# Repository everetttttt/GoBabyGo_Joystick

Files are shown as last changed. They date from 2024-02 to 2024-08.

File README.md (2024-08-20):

# GoBabyGo Joystick Project
### Wichita State University 2024
### Everett Kernen and Jackson Truitt
-----------
-----------

In this tutorial you will learn how to implement a joystick into your GoBabyGo vehicle for supporting children with motor or other disabilities.

## TODO
* add motor controller programmer details
* add linear actuator installation
* add images

You will need
-----------
### If you are at Wichita State, many of these components will already exist in the GoBabyGo room. Check before you purchase.
* [Vehicle](https://www.amazon.com/gp/product/B0C7JK9HNR/ref=ask_ql_qh_dp_hza?th=1)
     - This "Jeep" is the one we used and configured the steering mechanism for. Other ride-on vehicles we have seen use extremely similar electronics, so the only difference should be the steering.
* [Kill switch](https://www.amazon.com/Toggle-Switches-Rocker-Switch-Waterproof/dp/B07WW3WW3F)
* [Arduino Nano Every with headers](https://store-usa.arduino.cc/collections/boards-modules/products/arduino-nano-every-with-headers)
* [Motor Controller](https://www.amazon.com/HOBBYWING-QUICRUN-Waterproof-Brushed-Motors/dp/B07NYBF6MQ)
* [Motor Controller Programmer](https://www.hobbywingdirect.com/products/led-pc2c?variant=172030922)
     - The motor controller settings will be changed lower in this tutorial.
* [Linear Actuator](https://www.servocity.com/4-stroke-25-lb-thrust-linear-servo/)
     - At $300, this is by far the biggest opportunity we have to reduce costs. We are in the process of configuring [this servo,](https://www.amazon.com/GoolRC-Digital-Torque-Waterproof-Replacements/dp/B0B5H4MWZG) but that process is unfinished at this time.
* [Joystick](https://www.amazon.com/Acxico-Joystick-Potentiometer-JH-D202X-R2-Thermistor/dp/B09JZ8ZV4L)
* [RC Controller](https://www.amazon.com/DUMBORC-Transmitter-Receiver-Controller-400m-500m/dp/B07RR81GSB)
     - Used for parent override
* [30A bus bar](https://www.amazon.com/OONO-Position-Terminal-Distribution-Module/dp/B09D3BV22M)
* [4 foot servo wires](https://www.readymaderc.com/products/details/120cm-48in-jr-twisted-22awg-servo-cable?srsltid=AfmBOooBtGZkchE-u-FVPZSh1Mha9t9dLRYeGN2BnarDRjaqf-3A2QVKya4)
     - Quantity 2
* [Potentiometer - speed control](https://www.amazon.com/Uxcell-a15040700ux0380-Terminals-Linear-Potentiometer/dp/B019I13X5K)
* [Potentiometer - steering control](https://www.digikey.com/en/products/detail/bourns-inc/3296W-1-103LF/1088045)
     - Quantity 2
* [15 pin female header pins](https://www.amazon.com/2-54mm-Female-Single-Straight-Header/dp/B07VP63Z78)
     - Connect the arduino to the PCB
* [Male header pins](https://www.amazon.com/HiLetgo-20pcs-2-54mm-Single-Header/dp/B07R5QDL8D)
     - Connect everything else to the PCB
* [Spade connectors](https://www.amazon.com/Connectors-Shrink-Terminals-Female-MENTBERY/dp/B0BFDJNK91?source=ps-sl-shoppingads-lpcontext&ref_=fplfs&smid=A2TBO4E1CS6T20&th=1)
* PCB
     - You can upload the attached [gerber file](/GBG_Joystick_PCB_v4.zip) to a PCB manufacturer of your choice (PCBWay, JLCPCB, among others). You can also see and modify the [KiCAD files](/KiCAD/) and export from there.
     - Alternatively, you could build this on a breadboard or solder all wires together. If you do that, I highly recommend you reference the [schematic](/KiCAD/KiCAD.kicad_sch).
* Access to a soldering iron

## Starting here

After assembling your vehicle, the "engine bay" will look like this.
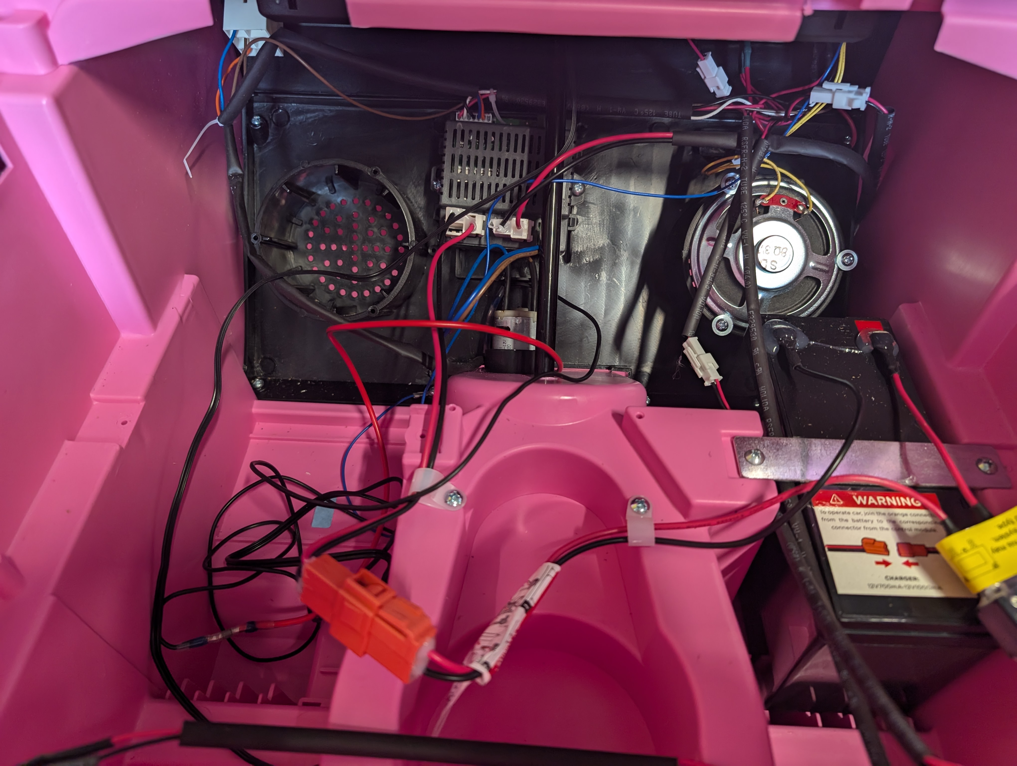
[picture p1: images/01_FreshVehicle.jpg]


It looks like (and is) a jumbled mess of wires, but it's pretty easy to sort out.
Here are the components that are relevant to us.
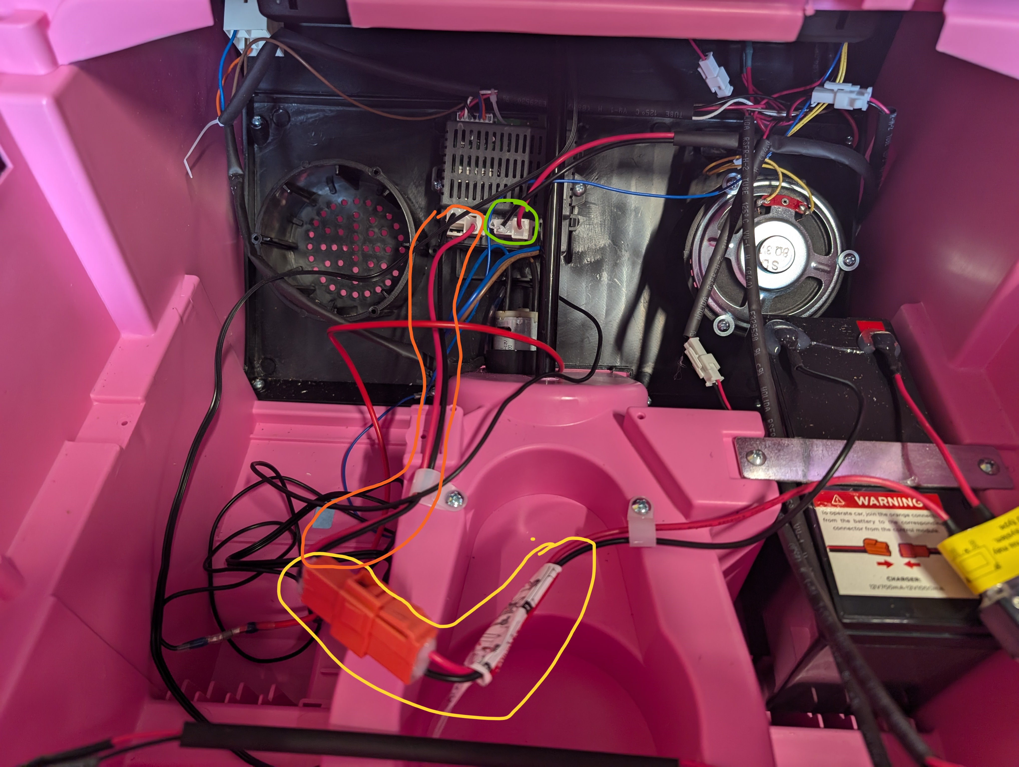
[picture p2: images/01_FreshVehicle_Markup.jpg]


## Step 1: Disassembly
1. Before you do anything, disconnect the battery, wires outlined in yellow.
2. Double check you've disconnected the battery. 
3. Disconnect the connector outlined in green. It heads to the rear motors which power the car.
4. Disconnect the connector leading to the steering motor. The connector is between the green and orange connectors and the wires are typically blue and brown.

## Step 2: Preparation and wiring power
Cut a small board to place all your components on. We used MDF, but it could be rigid cardboard.\
Gather your 30A bus, a spool of wire (14-18AWG), your kill switch, and your 30A bus.

### Preparation
1. Making sure once again that the orange wire is not connected on either side, cut it about three inches from the orange connector. 
2. Strip all four wires about a quarter of an inch
3. Take the red wire on the orange connector side and crimp on a spade connector that fits the wire guage. Once crimped, pull to make sure it is secure.
### Kill switch
4. Taking your spool of wire, strip the same amount from two wires and crimp the opposite spade connector on one. Again, pull to test it's secure, then connect it to the red wire we just crimped.
5. Run both spool wires from your spool to the rear of the car, running the wire along the bottom or side of the car to keep things neat and tidy. 
6. Use wire nuts or spade connectors to connect the wires to your kill switch.
7. Use a drill and the accompanying nuts that came with the switch to attach it securely to the rear of the car.
### 30A bus and motor controller
8. Coming back to the front, take the 30A bus and screw 1) the other wire from the kill switch and 2) the black wire on the orange connector side to the end of the bus. Note which letter is displayed. We used A for positive (red, going from battery positive to kill switch and back) and B for ground (black, battery negative).
9. Ensure the battery remains disconnected, if you connected it to test kill switch continuity.
10. Screw the power wires from the car controller (the other half of the orange wire) into the bus, ensuring A goes with A and B goes with B.
11. With your motor controller, cut and strip the red and black power wires and screw them into the bus.
12. Cut the connector (previously outlined in green) off the wires going to the rear motors. Strip both wires and crimp on spade connectors.
13. On the motor controller, cut and strip one yellow and one blue wire and crimp on the opposing spade connector.
14. Connect the motor controller and rear motor wires.

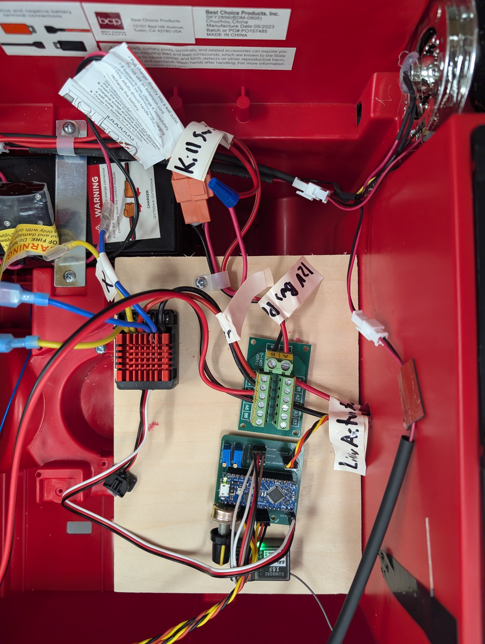
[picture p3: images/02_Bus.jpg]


Now referencing our [KiCAD schematic](images/02_schematic.png), we've completed the following (outlined in blue).
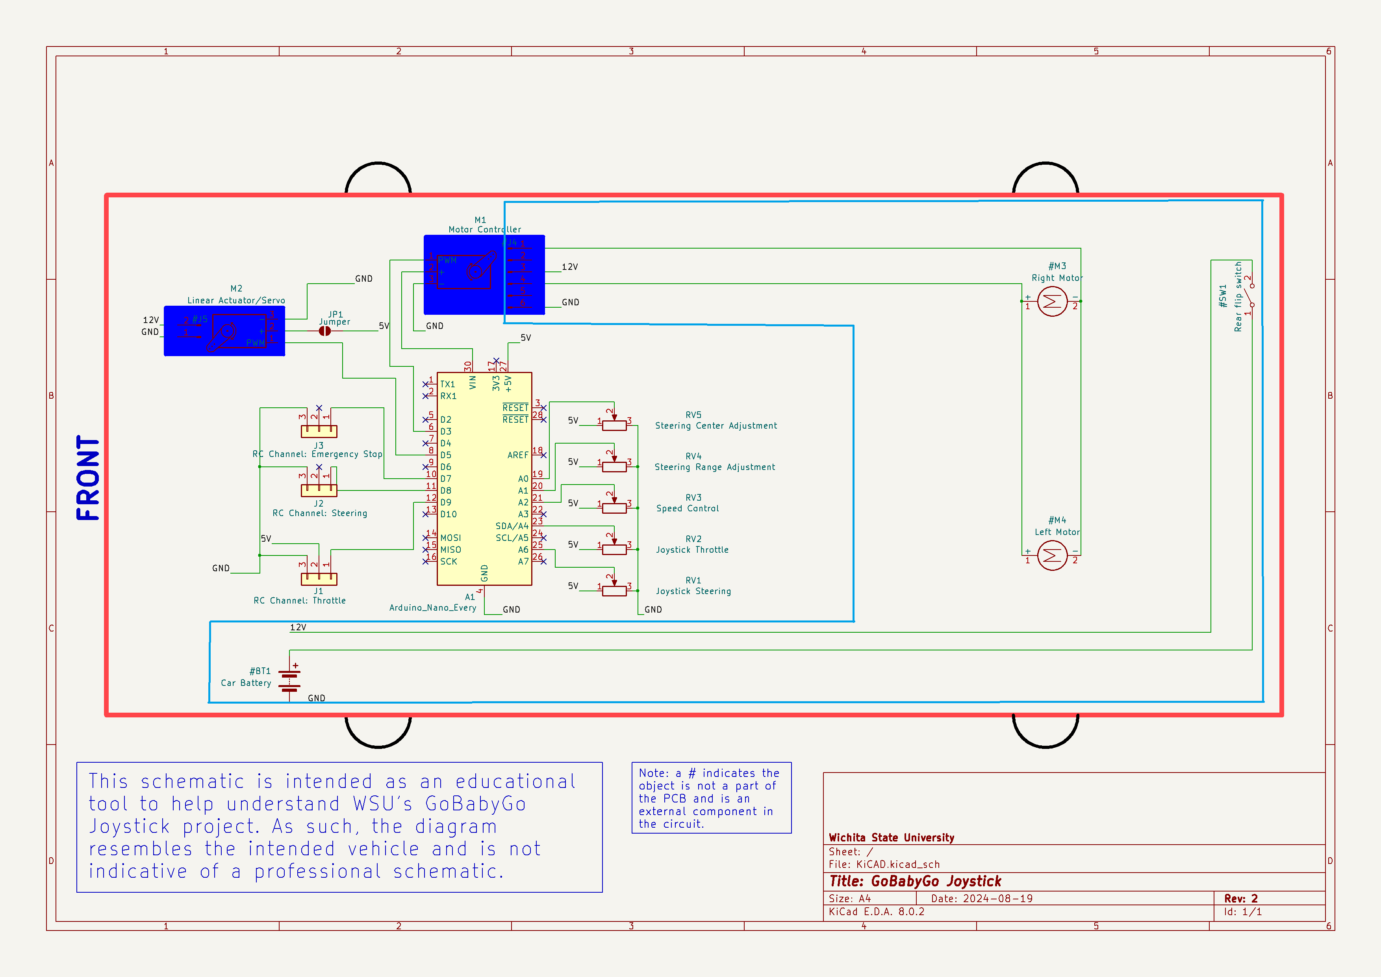
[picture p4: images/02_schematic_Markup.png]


## Step 3: Linear Actuator
### TODO

## Step 4: Joystick soldering
This soldering is easily the most difficult, so be prepared. We recommend grabbing some small heat shrink tubing to go over the wires to insulate and protect the connections.
1. Grab the joystick and two servo wires. Cut the wires and keep the female ends. We keep the female ends here because the 4 foot servo wires will connect their female ends to the male ends on the PCB.
2. Splice the wires, solder them to the joystick leads, and cover with heat shrink tubing.
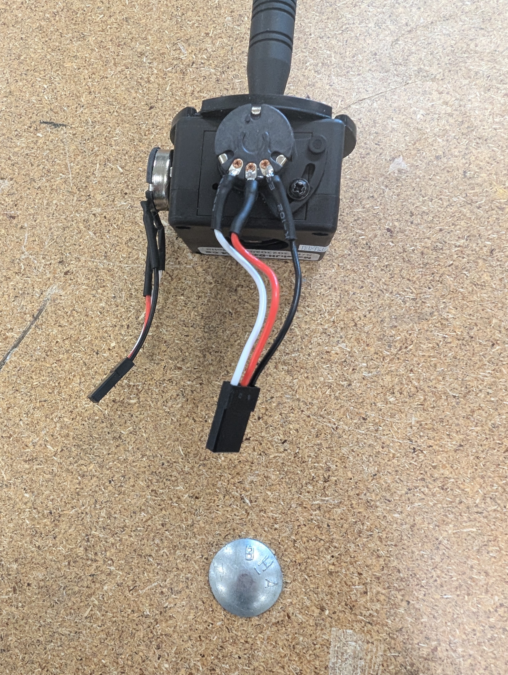
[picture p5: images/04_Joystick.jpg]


## Step 5: PCB
1. Gather your PCB, two 15 pin female headers, seven 3 pin male headers, and all three potentiometers.

2. Solder all components on the underside. When soldering the arduino headers, we recommend putting the arduino into the headers to ensure the two headers stay aligned.
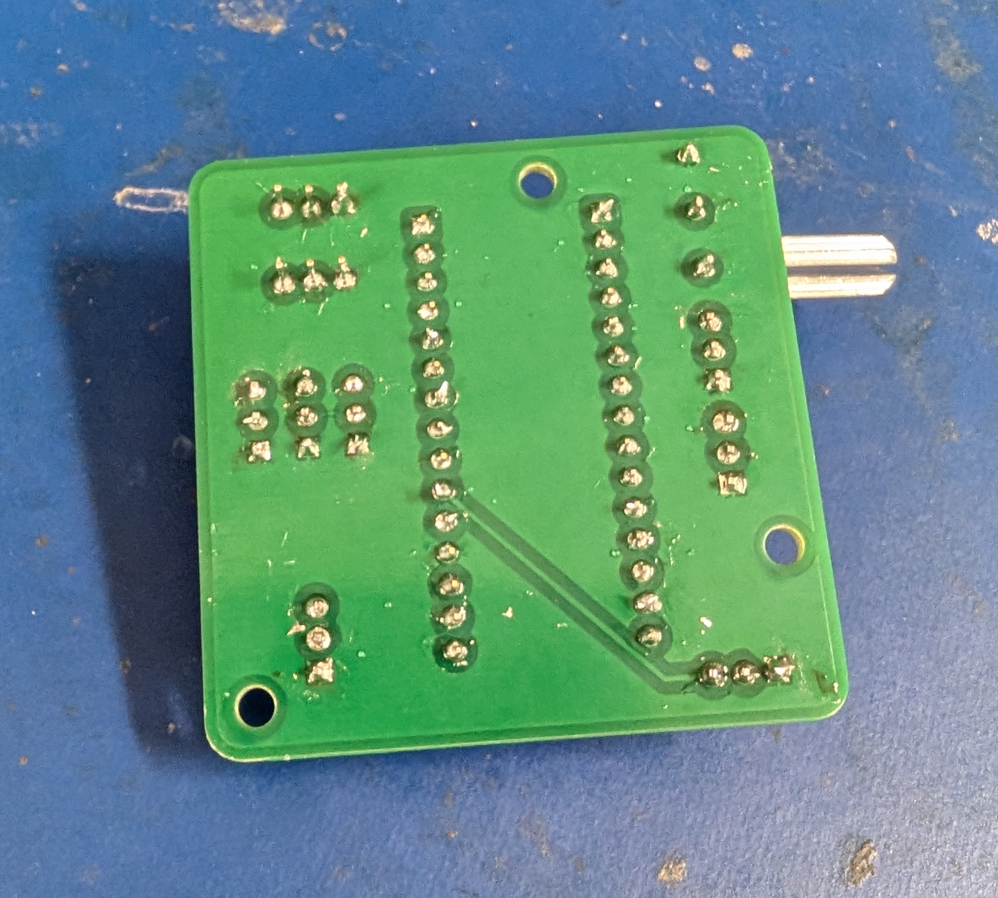
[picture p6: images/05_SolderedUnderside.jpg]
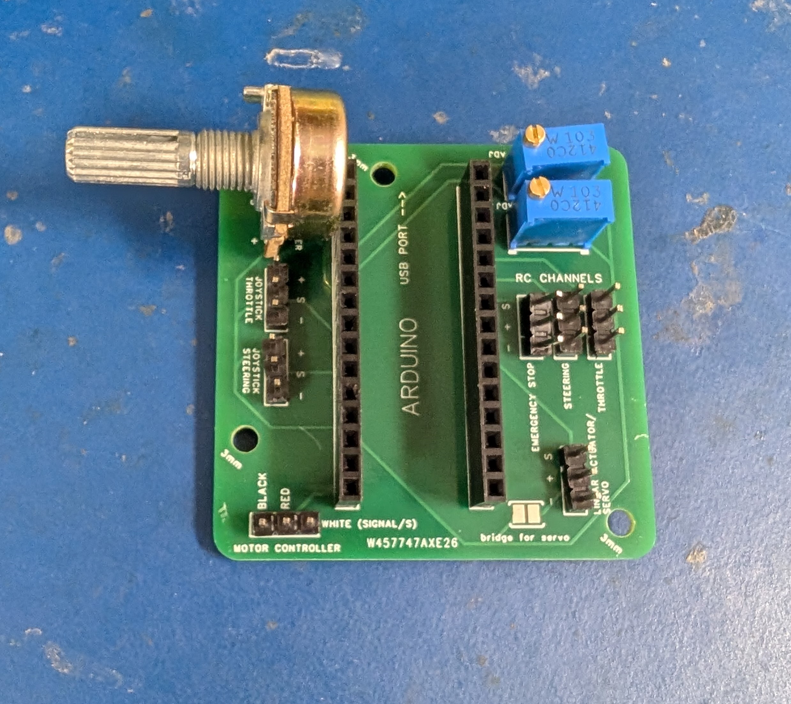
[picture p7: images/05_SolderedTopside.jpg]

3. Open the [Arduino sketch](/Arduino/Arduino.ino) in the Arduino IDE and flash the sketch to your arduino
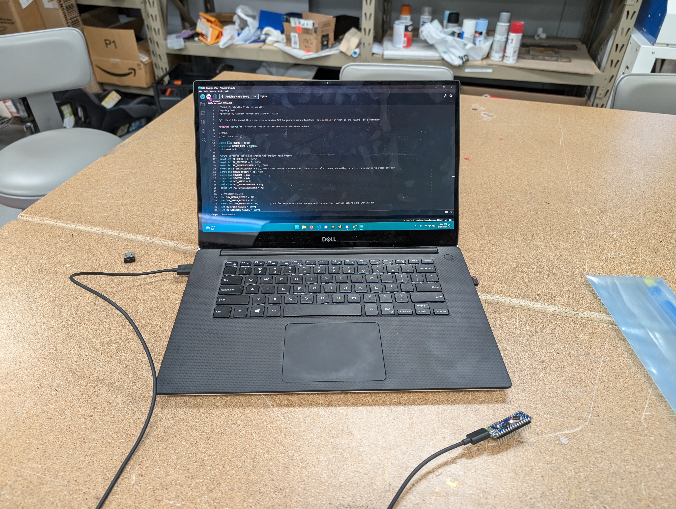
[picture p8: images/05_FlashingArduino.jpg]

### 4. Plug in all components to the PCB!!
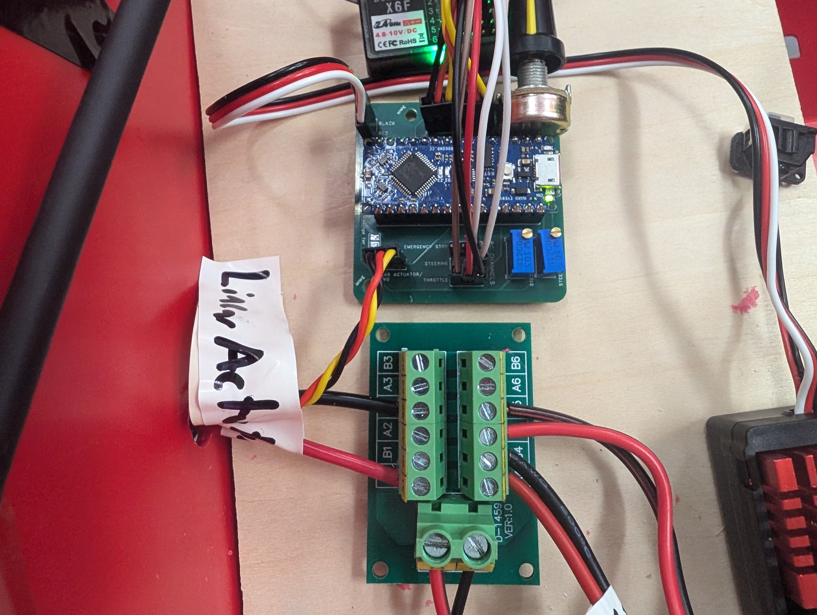
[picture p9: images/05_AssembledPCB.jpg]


## Step 6: RC controls
Grab the RC receiver and place it near the PCB. Tape the antenna where there will be little interference. Run jumper wires from the receiver to the PCB, according to the below picture.
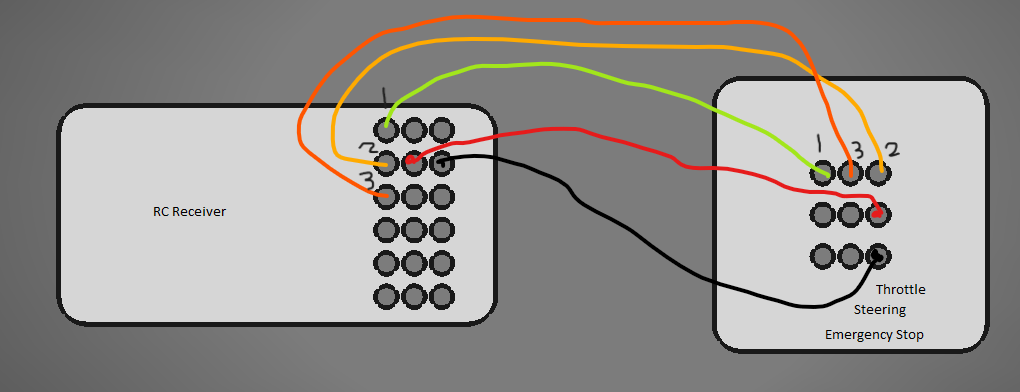
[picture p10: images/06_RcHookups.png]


## Step 7: Fine tuning

### Potentiometers
Plug the joystick extension wires into the PCB. Ensure nothing looks terribly wrong, then plug the battery in and flip the kill switch on.

If nothing looks amiss, turn the joystick right/left front/back. Turn the joystick until the directions are correct. If one of the two axis are flipped, simply unplug the connector from the PCB, turn it around, and plug it in again.

The vehicle should now have steering and motors functional. To increase or reduce the speed, turn the speed potentiometer until you are satisfied.

Next, flip the car or get into a position you can see the steering. It is likely not centered, so turn the steering center adjustment potentiometer until it is centered. Finally, move the joystick all the way in both directions, and reduce or increase the steering range adjustment potentiometer until the vehicle has maximum turning ability without running into the wheels or steering rack, etc.

### RC controls
Test the RC controller. Ensure the trigger controls the motor, the wheel controls steering, and the emergency stop button works as intended. If it has a different range or center than the joystick, open the top flap and adjust the knobs until it is much closer.

## Troubleshooting
If the car does not move when turned on, check that the RC controller is on. Occasionally, the RC receiver may, on start, send a signal that the emergency stop is on. Turning the controller on sends the proper signal to the receiver and the vehicle is free to move.

Ensure all components are fully seated into their connectors

Ensure the solder joints on the PCB make a proper connection.

If none of these work or if the vehicle motors/steering is wonky, connect the arduino to your computer and read the Serial Monitor. Check that the values there match up generally to what's written in the code. If you have trouble parsing the code, please feel free to open an issue in this github repo.

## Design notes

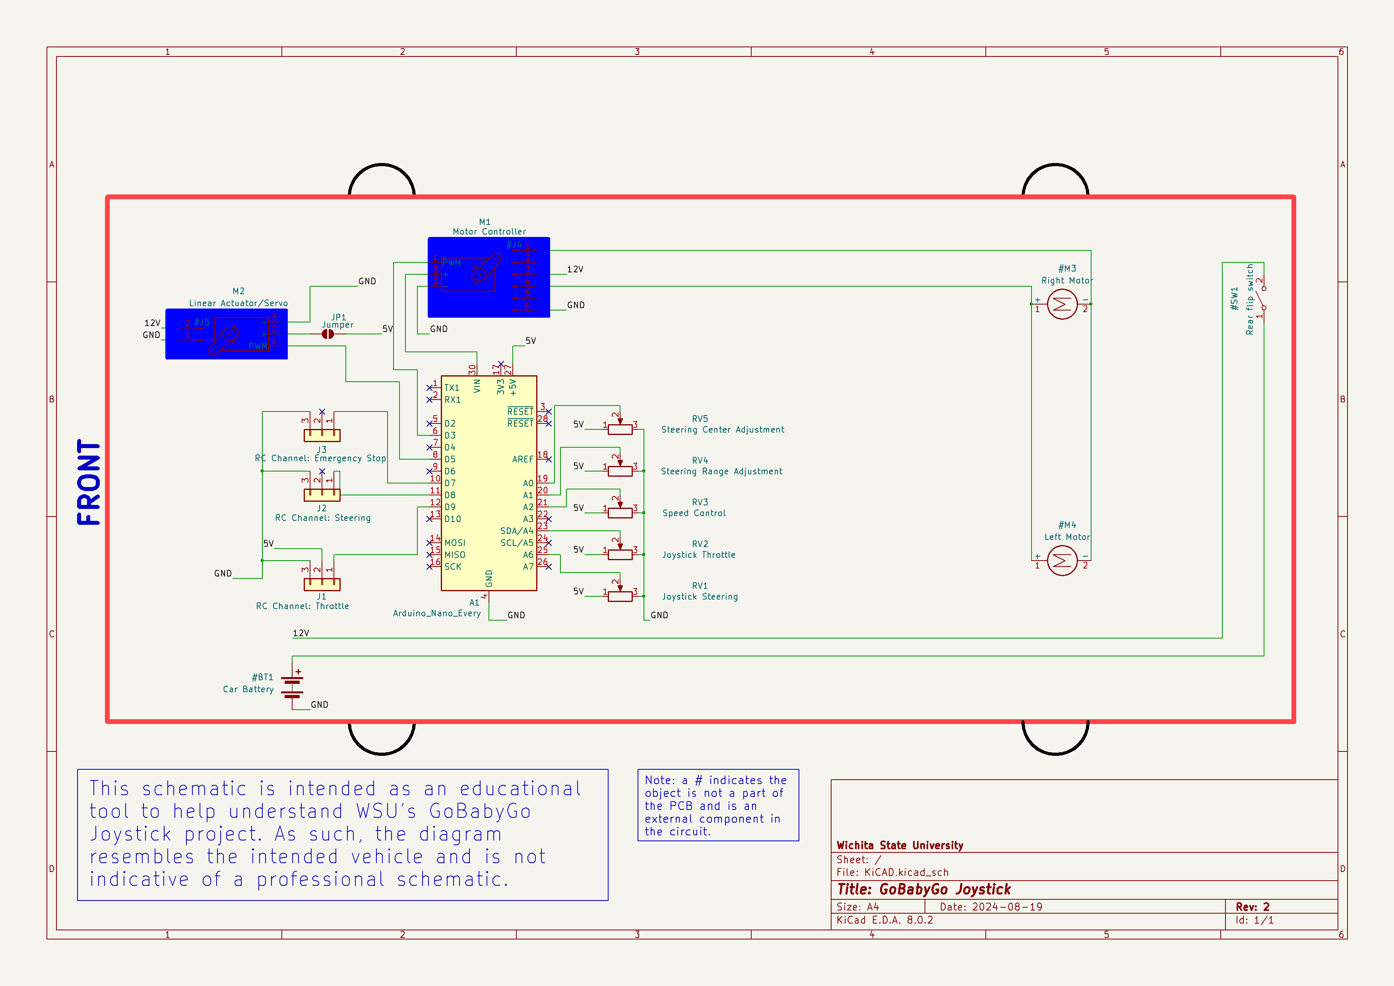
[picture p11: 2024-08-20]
images/02_schematic.png

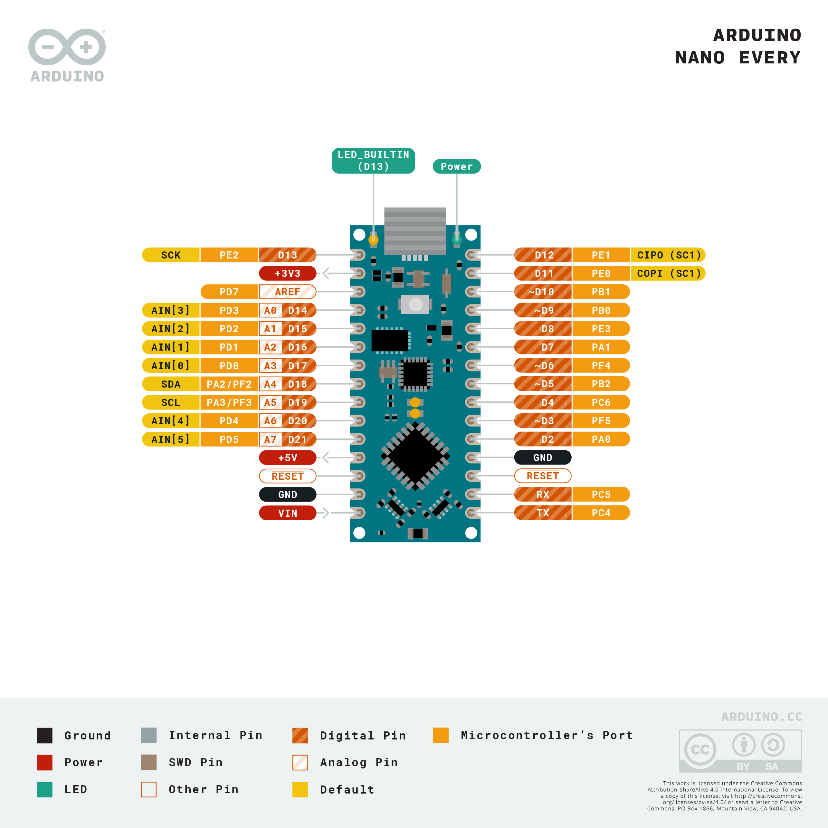
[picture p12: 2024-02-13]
nano_every_pinout.png

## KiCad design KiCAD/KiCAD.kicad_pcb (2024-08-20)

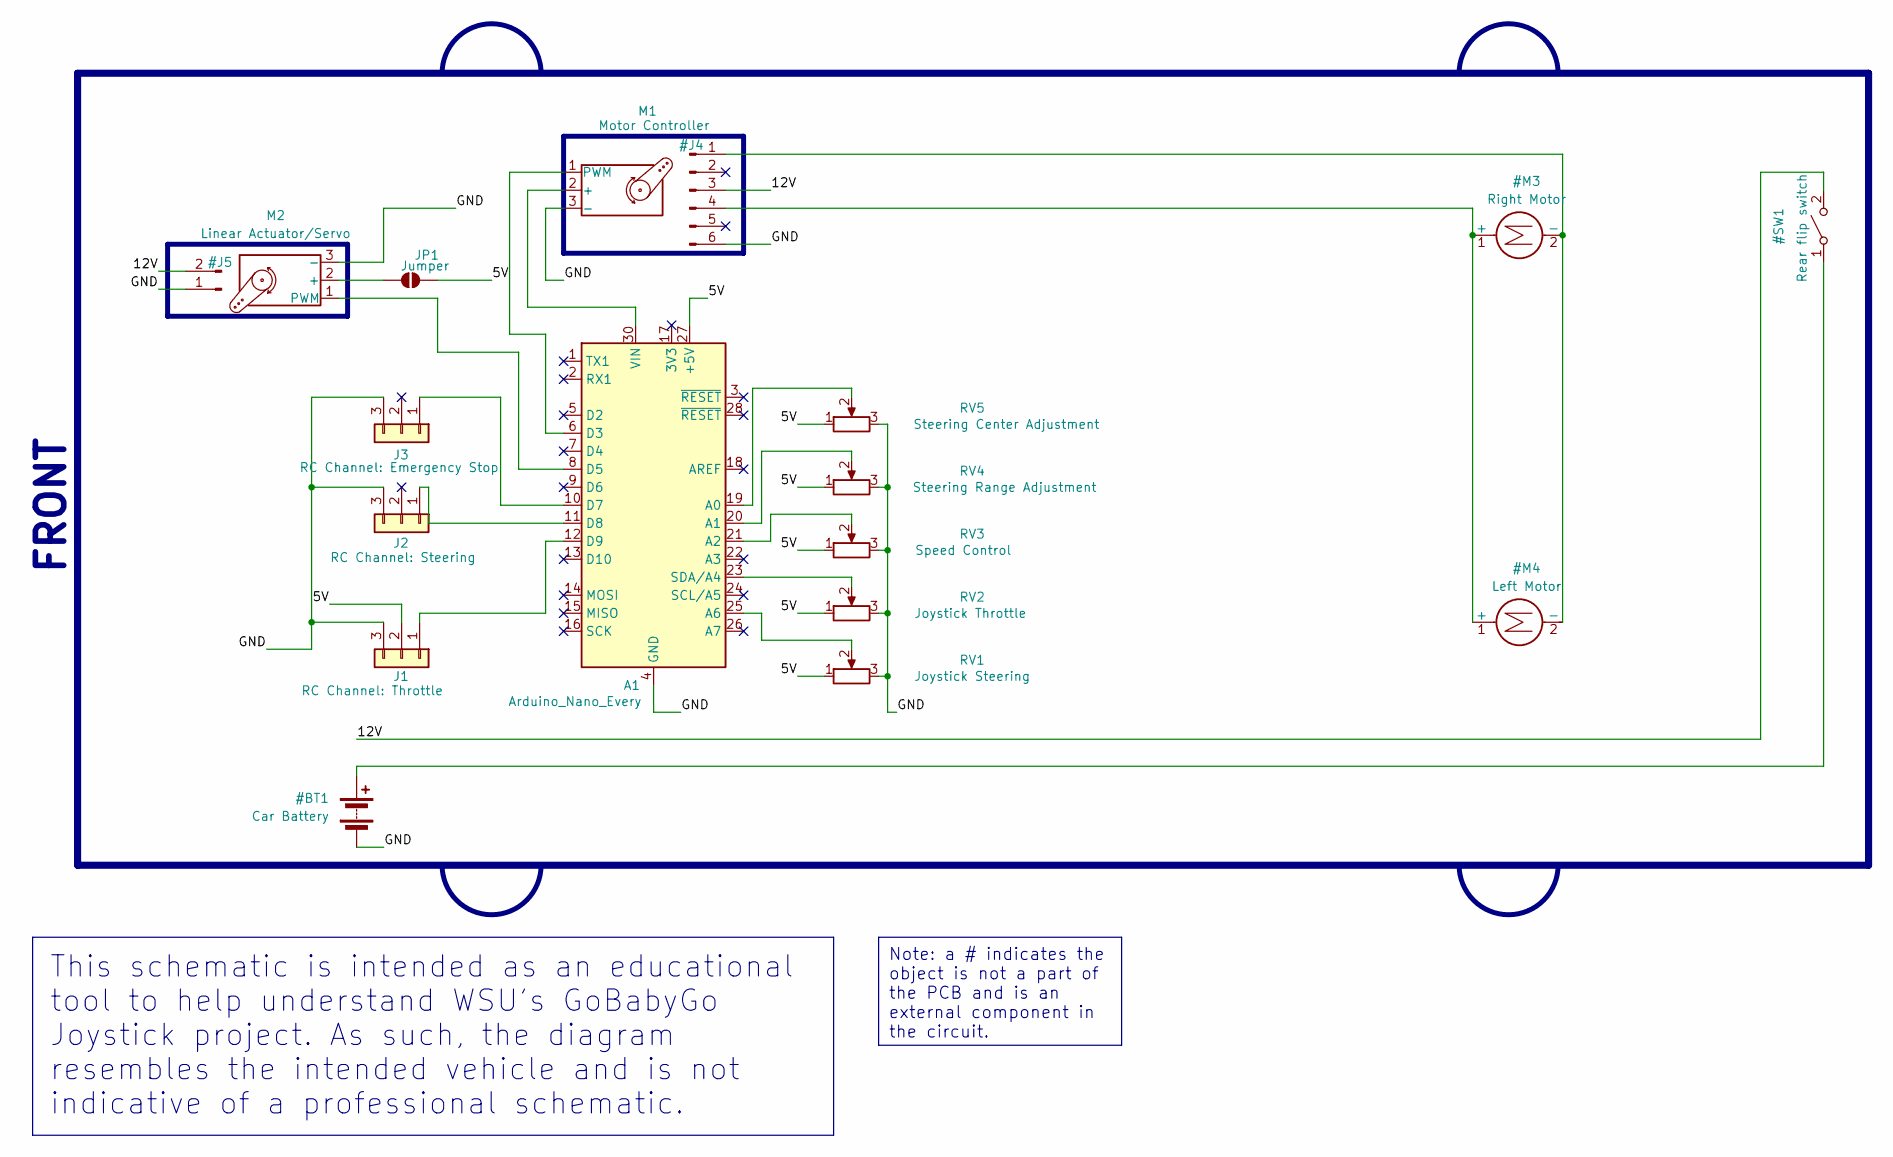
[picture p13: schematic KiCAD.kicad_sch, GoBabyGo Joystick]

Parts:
A1: Arduino_Nano_Every; Arduino_Nano
J1: RC Channel: Throttle; PinHeader_1x03_P2.54mm_Vertical
J2: RC Channel: Steering; PinHeader_1x03_P2.54mm_Vertical
J3: RC Channel: Emergency Stop; PinHeader_1x03_P2.54mm_Vertical
JP1: Jumper; SolderJumper-2_P1.3mm_Open_Pad1.0x1.5mm
M1: Motor Controller; PinHeader_1x03_P2.54mm_Vertical
M2: Linear Actuator/Servo; PinHeader_1x03_P2.54mm_Vertical
RV1: Joystick Steering; PinSocket_1x03_P2.54mm_Vertical
RV2: Joystick Throttle; PinSocket_1x03_P2.54mm_Vertical
RV3: Speed Control; PinHeader_1x05_P2.54mm_Vertical
RV4: Steering Range Adjustment; Potentiometer_Vishay_T93YA_Vertical
RV5: Steering Center Adjustment; Potentiometer_Vishay_T93YA_Vertical

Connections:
/5V: A1.27 (+5V), J1.2, JP1.2 (B), RV1.1, RV2.1, RV3.1, RV4.1, RV5.1
/GND: A1.4 (GND), A1.29 (GND), J1.3, J2.3, J3.3, M1.3 (-), M2.3 (-), RV1.3, RV2.3, RV3.3, RV4.3, RV5.3
unnamed: A1.19 (A0), RV5.2
unnamed: A1.20 (A1), RV4.2
unnamed: A1.21 (A2), RV3.2
unnamed: A1.25 (A6), RV1.2
unnamed: A1.6 (D3), M1.1 (PWM)
unnamed: A1.8 (D5), M2.1 (PWM)
unnamed: A1.10 (D7), J3.1
unnamed: A1.11 (D8), J2.1
unnamed: A1.12 (D9), J1.1
unnamed: A1.23 (SDA/A4), RV2.2
unnamed: A1.30 (VIN), M1.2 (+)
unnamed: JP1.1 (A), M2.2 (+)

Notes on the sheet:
This schematic is intended as an educational tool to help understand WSU's GoBabyGo Joystick project. As such, the diagram resembles the intended vehicle and is not indicative of a professional schematic.
Note: a # indicates the object is not a part of the PCB and is an external component in the circuit.
FRONT

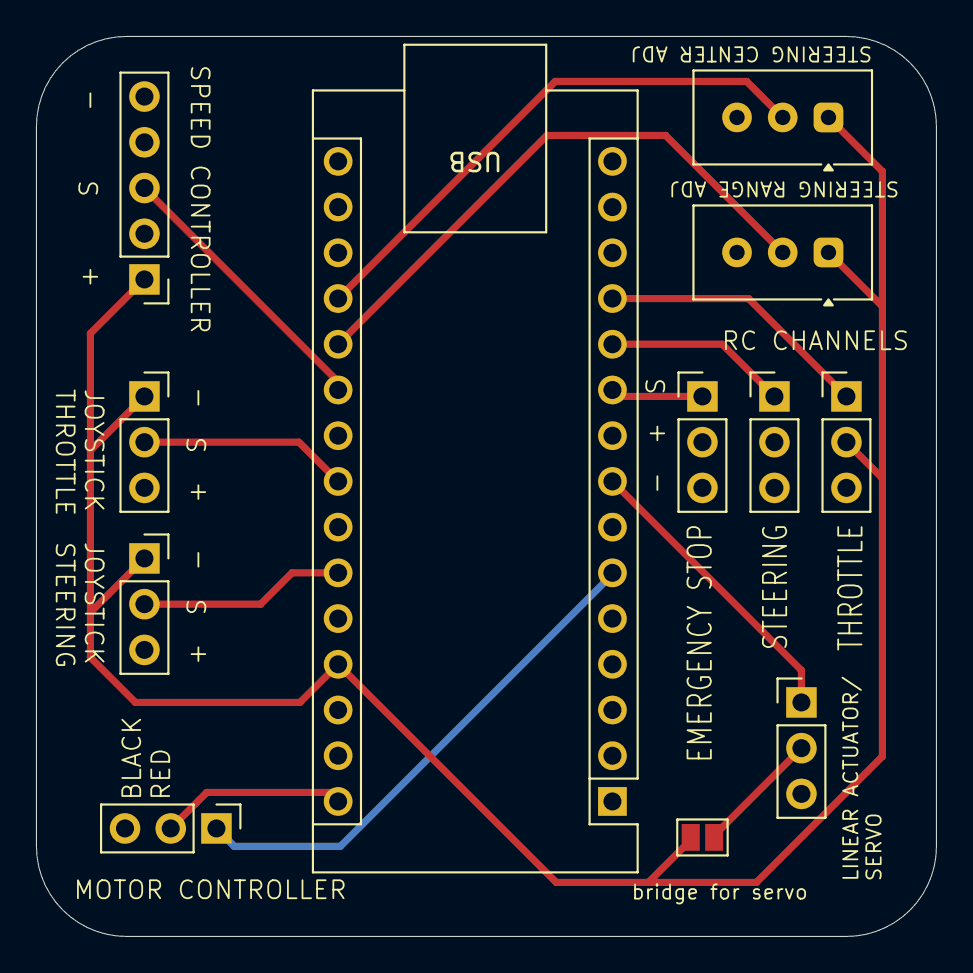
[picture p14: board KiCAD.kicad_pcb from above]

Board: 2 copper layers, 50.0 x 50.0 mm, 12 parts (0 on the bottom side), 14 nets.

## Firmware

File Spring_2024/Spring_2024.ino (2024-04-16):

//GoBabyGo Wichita State University
//Spring 2024
//project done by Everett Kernen, Joel Lewis, and Jacksn Truitt

//It should be noted this code uses a custom PCB to connect wires together. See details for that in the README, if I remember

#include <Servo.h> // enables PWM output to the drive and steer motors

//TODO:
//test (obviously)
//set up emergency stop func


//PINS (ordered clockwise around the arduino nano every)
const int JOYSTICKSWITCH = 12;
const int RC_SPEED = 9; //PWM  10 9 6
const int RC_STEERING = 8; //PWM
const int RC_EMERGENCYSTOP = 7; //PWM
const int STEERING_output = 5; //PWM - this controls either the linear actuator or servo, depending on which is selected to steer the car
const int MOTOR_output = 3; //PWM
const int SPEEDCONTROLLER = A0;
const int JOYHORI = A2;
const int JOYVERT = A4;
const int STEERINGADJUSTMENT = A6;

//CONSTANT VALUES
int JOY_MOTOR_MIDDLE = 0;
int JOY_STEER_MIDDLE = 0;
const int JOY_DEADZONE = 130;         //how far away from center do you need to push the joystick before it's initialized?
int RC_SPEED_MIDDLE = 50;
int RC_STEERING_MIDDLE = 50;
int RC_STOP_MIDDLE = 50;
const int RC_DEADZONE = 25;

const int motor_maxDistanceFromZero = 400; // distance from fwdSpeed and bwdSpeed, used for speed controller
int motor_bwdSpeed = 1100;
const int motor_zeroSpeed = 1500;
int motor_fwdSpeed = 1900;
const int motor_brakeBuffer = 100;

const int steering_distanceFromZero = 250;
int steering_left = 1250;
int steering_middle = 1500;
int steering_right = 1750;



//VARIABLES
int joy_motorValue;
int joy_steerValue;
int speedValue;

//Motor Controller (viewed by arduino as a servo), see https://www.arduino.cc/reference/en/libraries/servo/writemicroseconds/ for how we are controlling the "Servos"
Servo MOTOR;
Servo STEER;


// see https://www.arduino.cc/reference/en/language/functions/external-interrupts/attachinterrupt/ for info on interrupts, Interrupt Service Routines (ISRs), etc.
class PWM {
  int pin;
  bool prevState;
  unsigned long time;
  int value = -1; // given in terms of a duty cycle percentage
  unsigned int timeLow = 0;
  unsigned int timeHigh = 0;

  public:
    PWM(int pwm_pin) {
      pin = pwm_pin;
    }
    void start() {
      prevState = digitalRead(pin);
      time = micros();
      pinMode(pin, INPUT);
    }

    int GetValue() { return (value == -1 ? 50 : value); }

    void InterruptServiceRoutine() {
      unsigned long currTime = micros();
      bool currState = digitalRead(pin);
      if (currState != prevState) {
        if (currState) { // switched from low to high
          time = currTime;
          //timeLow = currTime - time;
          //time = currTime;
          //value = (int)((timeHigh / (timeLow + timeHigh)) * 100);
            // value = percentage of time high
        } 
        else { // switched from high to low
          //timeHigh = currTime - time;
          value = (int)(currTime - time);
          time = currTime;
        }
        prevState = currState;
      }
    }
};

//PWM class allows us to read PWM signals from the RC receiver using interrupts instead of pulseIn which can be slow
PWM rc_motor(RC_SPEED);
PWM rc_steer(RC_STEERING);
PWM rc_stop(RC_EMERGENCYSTOP);

// -------------------FUNCTIONS START HERE//------------------- //

// put your setup code here, to run once:
void setup() {

  Serial.begin(9600);   //tells arduino how fast to interact with the Serial Monitor

  //set input and output pins for arduino
  pinMode(JOYSTICKSWITCH, INPUT);
  pinMode(SPEEDCONTROLLER, INPUT);
  pinMode(JOYHORI, INPUT);
  pinMode(JOYVERT, INPUT);
  
  rc_motor.start();
  attachInterrupt(digitalPinToInterrupt(RC_SPEED), RCMotorInterrupt, CHANGE);
  rc_steer.start();
  attachInterrupt(digitalPinToInterrupt(RC_STEERING), RCSteerInterrupt, CHANGE);
  rc_stop.start();
  attachInterrupt(digitalPinToInterrupt(RC_EMERGENCYSTOP), RCStopInterrupt, CHANGE);
  
  MOTOR.attach(MOTOR_output);
  STEER.attach(STEERING_output);

  MOTOR.writeMicroseconds(motor_zeroSpeed);
  STEER.writeMicroseconds(steering_middle);

  setConstants();

  pinMode(12, OUTPUT);
  digitalWrite(12, HIGH);
  pinMode(10, OUTPUT);
  digitalWrite(10, LOW);  
}
int print = 0;
// put your main code here, to run repeatedly:
void loop() {

  //take in analog input to read what values the joystick is sending
  joy_motorValue = analogRead(JOYVERT);
  joy_steerValue = analogRead(JOYHORI);

  //read speed controller and set speed values
  //SetSpeed();
  //SetSteering();


  //print out values to the serial monitor so that we can look at them
  if (print == 1500){
    Serial.print("Joy motor:          ");
    Serial.println(joy_motorValue);
    Serial.print("Joy steer:          ");
    Serial.println(joy_steerValue);
    Serial.print("RC motor:           ");
    Serial.println(rc_motor.GetValue());
    Serial.print("RC steer:           ");
    Serial.println(rc_steer.GetValue());
    Serial.print("RC Emergency Stop:  ");
    Serial.println(rc_stop.GetValue());
    Serial.println();
    print = 0;
  }
  print++;


  // TEST FOR EMERGENCY STOP
  if (false && (rc_stop.GetValue() < RC_STOP_MIDDLE - RC_DEADZONE ||
      rc_stop.GetValue() > RC_STOP_MIDDLE + RC_DEADZONE)) {
    EmergencyStop();
  }

  // SEND SIGNAL TO MOTOR
  if (false && (rc_motor.GetValue() < RC_STOP_MIDDLE - RC_DEADZONE ||
      rc_motor.GetValue() > RC_STOP_MIDDLE + RC_DEADZONE)) { // prioritize the rc controller
    MOTOR.writeMicroseconds(rc_motor.GetValue());
  }
  else if (joy_motorValue > JOY_MOTOR_MIDDLE + JOY_DEADZONE ||
            joy_motorValue < JOY_MOTOR_MIDDLE - JOY_DEADZONE) {
      int speed = map(joy_motorValue, 0, 1023, motor_bwdSpeed, motor_fwdSpeed);
      MOTOR.writeMicroseconds(speed);
  }
  else {
    MOTOR.writeMicroseconds(motor_zeroSpeed);
  }


  // SEND SIGNAL TO STEERING
  if (false && (rc_steer.GetValue() < RC_STOP_MIDDLE - RC_DEADZONE ||
      rc_steer.GetValue() > RC_STOP_MIDDLE + RC_DEADZONE)) { // prioritize the rc controller
    STEER.writeMicroseconds(rc_steer.GetValue());
  }
  else if (joy_steerValue > JOY_STEER_MIDDLE + JOY_DEADZONE ||
            joy_steerValue < JOY_STEER_MIDDLE - JOY_DEADZONE) {
      int steer = map(joy_steerValue, 0, 1023, steering_left, steering_right);
      STEER.writeMicroseconds(steer);
  }
  else {
    STEER.writeMicroseconds(steering_middle);
  }

}

// ----------- HELPER FUNCTIONS ----------- //

void setConstants() {
  JOY_MOTOR_MIDDLE = analogRead(JOYVERT);
  JOY_STEER_MIDDLE = analogRead(JOYHORI);
}

void SetSpeed() {
  speedValue = analogRead(SPEEDCONTROLLER);
  speedValue /= 128; // cut down to values between 0 and 7, inclusive
  speedValue++; // 1 to 8
  int distFromZero = (int)(motor_maxDistanceFromZero / 3) + (int)(motor_maxDistanceFromZero / 12 * speedValue);
    //distFromZero is split into 8 sections in the top two thirds of motor_maxDistanceFromZero
  motor_fwdSpeed = motor_zeroSpeed + distFromZero;
  motor_bwdSpeed = motor_zeroSpeed - distFromZero;
}

void SetSteering() {
  int steerValue = analogRead(STEERINGADJUSTMENT);
  steerValue = map(steerValue, 0, 1023, -100, 100);
  steering_middle = 1500 + steerValue;
  steering_left = steering_middle + steering_distanceFromZero;
  steering_right = steering_middle - steering_distanceFromZero;

}

void EmergencyStop() {
  // does rc send stop consistently? or just once?
  // if consistently, wait for release of button
  //while (rc_stop);
}

void RCMotorInterrupt() { rc_motor.InterruptServiceRoutine(); }
void RCSteerInterrupt() { rc_steer.InterruptServiceRoutine(); }
void RCStopInterrupt() { rc_stop.InterruptServiceRoutine(); }

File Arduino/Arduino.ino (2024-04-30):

//GoBabyGo Wichita State University
//Spring 2024
//project by Everett Kernen and Jackson Truitt

//It should be noted this code uses a custom PCB to connect wires together. See details for that in the README, if I remember

#include <Servo.h> // enables PWM output to the drive and steer motors

//TODO:
//test (obviously)

const bool DEBUG = true;
const int DEBUG_FREQ = 10000;
int count = 0;

//PINS (ordered clockwise around the arduino nano every)
const int RC_SPEED = 9; //PWM
const int RC_STEERING = 8; //PWM
const int RC_EMERGENCYSTOP = 7; //PWM
const int STEERING_output = 5; //PWM - this controls either the linear actuator or servo, depending on which is selected to steer the car
const int MOTOR_output = 3; //PWM
const int JOYHORI = A6;
const int JOYVERT = A4;
const int ADJ_SPEED = A2;
const int ADJ_STEERINGRANGE = A1;
const int ADJ_STEERINGCENTER = A0;

//CONSTANT VALUES
int JOY_MOTOR_MIDDLE = 512;
int JOY_STEER_MIDDLE = 512;
const int JOY_DEADZONE = 100;         //how far away from center do you need to push the joystick before it's initialized?
int RC_SPEED_MIDDLE = 1500;
int RC_STEERING_MIDDLE = 1500;
int RC_STOP_MIDDLE = 1300;
const int RC_DEADZONE = 250;

const int motor_maxDistanceFromZero = 400; // distance from fwdSpeed and bwdSpeed, used for speed controller
int motor_bwdSpeed = 1100;
const int motor_zeroSpeed = 1500;
int motor_fwdSpeed = 1900;

const int steering_maxDistanceFromZero = 500;
int steering_left = 1300;
int steering_middle = 1500;
int steering_right = 1700;



//VARIABLES
int joy_motorValue;
int joy_steerValue;
int adj_speed;
int adj_steerCenter;
int adj_steerRange;

//Motor Controller (viewed by arduino as a servo), see https://www.arduino.cc/reference/en/libraries/servo/writemicroseconds/ for how we are controlling the "Servos"
Servo MOTOR;
Servo STEER;


// see https://www.arduino.cc/reference/en/language/functions/external-interrupts/attachinterrupt/ for info on interrupts, Interrupt Service Routines (ISRs), etc.
class PWM {
  int pin;
  bool prevState;
  unsigned long time;
  int value = -1;

  public:
    PWM(int pwm_pin) {
      pin = pwm_pin;
    }
    void start() {
      prevState = digitalRead(pin);
      time = micros();
      pinMode(pin, INPUT);
    }

    int GetValue() { return value; }

    void InterruptServiceRoutine(int rc) {
      unsigned long currTime = micros();
      bool currState = digitalRead(pin);
      if (currState != prevState) {
        if (currState) { // switched from low to high
          time = currTime;
        } 
        else { // switched from high to low
          value = currTime - time;
          /*
          switch (rc) { // set rc middle values if not yet set
            case 0:
              RC_SPEED_MIDDLE = (RC_SPEED_MIDDLE == -1 ? value : RC_SPEED_MIDDLE);
              break;
            case 1:
              RC_STEERING_MIDDLE = (RC_STEERING_MIDDLE == -1 ? value : RC_STEERING_MIDDLE);
              break;
            case 2:
              RC_STOP_MIDDLE = (RC_STOP_MIDDLE == -1 ? value : RC_STOP_MIDDLE);
              break;
          }
          */
        }
        prevState = currState;
      }
    }
};

//PWM class allows us to read PWM signals from the RC receiver using interrupts instead of pulseIn which can be slow
PWM rc_motor(RC_SPEED);
PWM rc_steer(RC_STEERING);
PWM rc_stop(RC_EMERGENCYSTOP);

// -------------------FUNCTIONS START HERE//------------------- //

// put your setup code here, to run once:
void setup() {
  Serial.begin(9600);   //tells arduino how fast to interact with the Serial Monitor

  //set input and output pins for arduino
  pinMode(JOYHORI, INPUT);
  pinMode(JOYVERT, INPUT);
  pinMode(ADJ_SPEED, INPUT);
  pinMode(ADJ_STEERINGRANGE, INPUT);
  pinMode(ADJ_STEERINGCENTER, INPUT);
  
  rc_motor.start();
  attachInterrupt(digitalPinToInterrupt(RC_SPEED), RCMotorInterrupt, CHANGE);
  rc_steer.start();
  attachInterrupt(digitalPinToInterrupt(RC_STEERING), RCSteerInterrupt, CHANGE);
  rc_stop.start();
  attachInterrupt(digitalPinToInterrupt(RC_EMERGENCYSTOP), RCStopInterrupt, CHANGE);
  
  MOTOR.attach(MOTOR_output);
  STEER.attach(STEERING_output);

  MOTOR.writeMicroseconds(motor_zeroSpeed);
  STEER.writeMicroseconds(steering_middle);

  setMiddles();
}

// put your main code here, to run repeatedly:
void loop() {

  //take in analog input to read what values the joystick is sending
  joy_motorValue = analogRead(JOYVERT);
  joy_steerValue = analogRead(JOYHORI);

  //read speed controller and set speed values
  //SetSpeed();
  SetSteer();


  //print out values to the serial monitor so that we can look at them
  if (DEBUG && count == DEBUG_FREQ) {
    Serial.print("Joy motor:          ");
    Serial.print(joy_motorValue);
    Serial.print("   Motor Middle:      ");
    Serial.println(JOY_MOTOR_MIDDLE);

    Serial.print("Joy steer:          ");
    Serial.print(joy_steerValue);
    Serial.print("   Steer Middle:      ");
    Serial.println(JOY_STEER_MIDDLE);

    Serial.print("RC motor:           ");
    Serial.print(rc_motor.GetValue());
    Serial.print("  RC Motor Middle:    ");
    Serial.println(RC_SPEED_MIDDLE);

    Serial.print("RC steer:           ");
    Serial.print(rc_steer.GetValue());
    Serial.print("  RC Steer Middle:    ");
    Serial.println(RC_STEERING_MIDDLE);

    Serial.print("RC Emergency Stop:  ");
    Serial.print(rc_stop.GetValue());
    Serial.print("  RC Stop Middle:    ");
    Serial.println(RC_STOP_MIDDLE);
    Serial.println();
    count = 0;
  }
  count++;

  // TEST FOR EMERGENCY STOP
  if (rc_stop.GetValue() > (RC_STOP_MIDDLE + RC_DEADZONE) || rc_stop.GetValue() < (RC_STOP_MIDDLE - RC_DEADZONE)) {
    Serial.println("EMERGENCY STOP ACTIVATED");
    EmergencyStop();
  }

  // TEST FOR RC INPUTS
  if (rc_motor.GetValue() > (RC_SPEED_MIDDLE + RC_DEADZONE) || rc_motor.GetValue() < (RC_SPEED_MIDDLE - RC_DEADZONE) ||
      rc_steer.GetValue() > (RC_STEERING_MIDDLE + RC_DEADZONE) || rc_steer.GetValue() < (RC_STEERING_MIDDLE - RC_DEADZONE)) { // prioritize the rc controller
    Serial.println("RC OVERRIDE");
    if (rc_motor.GetValue() > (RC_SPEED_MIDDLE + RC_DEADZONE) || rc_motor.GetValue() < (RC_SPEED_MIDDLE - RC_DEADZONE)) {
      int speed = map(rc_motor.GetValue(), 1000, 2000, motor_bwdSpeed, motor_fwdSpeed);
      MOTOR.writeMicroseconds(speed);
    }
    else {
      MOTOR.writeMicroseconds(motor_zeroSpeed);
    }

    if (rc_steer.GetValue() > (RC_STEERING_MIDDLE + RC_DEADZONE) || rc_steer.GetValue() < (RC_STEERING_MIDDLE - RC_DEADZONE)) {
      int steer = map(rc_steer.GetValue(), 1000, 2000, steering_left, steering_right);
      STEER.writeMicroseconds(steer);
    }
    else {
      STEER.writeMicroseconds(steering_middle);
    }
  }
  else {
    // SEND SIGNAL TO MOTOR
    if (joy_motorValue > (JOY_MOTOR_MIDDLE + JOY_DEADZONE) || joy_motorValue < (JOY_MOTOR_MIDDLE - JOY_DEADZONE)) { // test for joystick input
      int speed = map(joy_motorValue, 0, 1023, motor_bwdSpeed, motor_fwdSpeed);
      MOTOR.writeMicroseconds(speed);
    }
    else {
      MOTOR.writeMicroseconds(motor_zeroSpeed);
    }
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

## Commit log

2024-01-24 Adding previously working arduino code and a test template for seeing what the linear actuator will output
2024-01-24 added wiring diagram for previous working version (no linear actuator)
2024-02-13 added motor controller test
2024-04-10 updated email and added wiring diagram from previous year
2024-04-10 fully rewrote arduino file for pcb and using servo controls for both motors and steering
2024-04-15 added pcb gerber file
2024-04-15 new pcb
2024-04-18 cleaned up and moved files around, replaced PCB gerber v2 with the final v4
2024-08-19 Added KiCAD files and documentation photos
    [WSU GoBabyGo.kicad_pcb, WSU GoBabyGo.kicad_sch]
2024-08-20 Renamed arduino script and removed old wiring diagrams
2024-08-20 Remade KiCAD files
    [KiCAD.kicad_pcb, KiCAD.kicad_sch, WSU GoBabyGo.kicad_pcb]
2024-08-20 Fixed assembled PCB image
